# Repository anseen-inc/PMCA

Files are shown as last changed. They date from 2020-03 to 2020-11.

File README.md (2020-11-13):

# ポケットMCA（PSoC）
ポケットMCA（PSoC）（以下PMCA）は、PSoC 5LPを用いた簡易Multi Channel Analyzer (MCA)です。
MCA機能をPSoC内のブロックで構成し外付け部品を極力廃しているため、[CY8CKIT-059 PSoC® 5LP Prototyping Kit](https://www.cypress.com/documentation/development-kitsboards/cy8ckit-059-psoc-5lp-prototyping-kit-onboard-programmer-and)に1μFの容量と1kΩの抵抗を加えることでMCAとして動作します。

## 入力信号経路

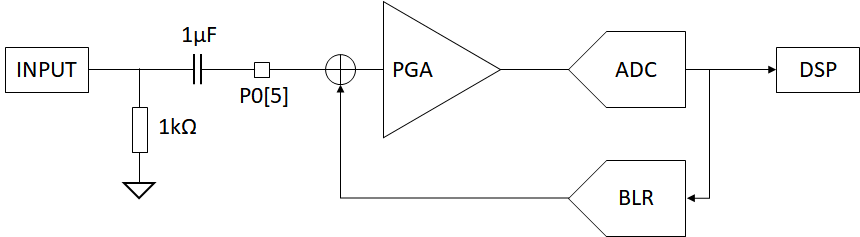
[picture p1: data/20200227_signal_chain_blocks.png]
信号経路

この図はPSoC内を含めた入力信号経路を示しています。
AC結合された入力信号はPGA（Programmable Gain Amplifier）で増幅した後、ADCでデジタル化されます。
デジタル化された信号は後段のDSP（Digital Signal Processing）ブロックに渡され、波高値情報が抽出されます。
並行してBLRブロックにもデジタル値が渡され、PGAの入力にフィードバックすることでベースライン電位が再設定されます。

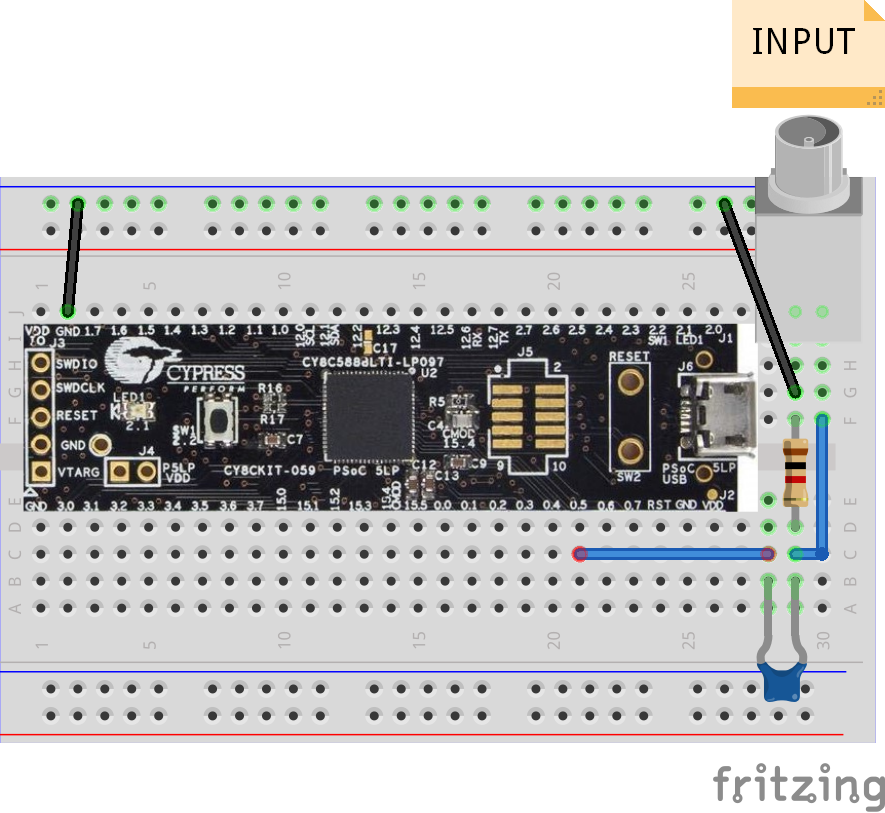
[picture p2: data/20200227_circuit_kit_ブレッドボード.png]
Prototyping Kitを用いる場合の接続

Prototyping KitでMCAを構成する場合には、図のように1μFの容量と1kΩの抵抗を入力端子に接続してください。

## 仕様

|項目|値|補足|
|:--|:--|:--|
|電源電圧|5V±0.25V|USBハイパワーポートの範囲（4.75V~5.25V）|
|消費電流（MCA)|20mA||
|入力電圧範囲|±10V|AC結合容量に依存|
|信号電圧範囲|±2Vpp max.|ゲイン2倍時|
|ピークタイム|10μs以上|満たない場合でも測定は可能|
|最大カウントレート|100kcps||

## 使い方
PMCA用の[ファームウェア書き込み](#HEXファイル書き込み)後、Windows PCとUSBケーブルで接続することでCOMポートとして認識されます。
そのCOMポートに対してASCIIコードを送ることでPMCAと対話でき、動作の変更や測定が行えます。
最初のアルファベットでコマンド種別を選択し、続く16進数（0~F）で設定値を指定します。
設定値がある場合は制御コマンド、ない場合は読み出しコマンドとして判断されます。
最初のアルファベット、コマンド指定以降の16進数以外は無視されます。

コマンドの例

```
SA # 10秒の測定を開始
S A # 上と同じ
V 3FC # HVを1020Vに設定
V # HV出力のモニタ結果を読み出す
```

PCから送信するコマンドの終端は改行（CR）です。
PMCAから送信するデータの終端は4 byte NULL（0x00000000）となっており、NULL終端文字列として取り込めます。
実際には端末エミュレータ互換のためNULLの前に改行（CR）が存在します。
加えて、データの成否を表す'OK/NG'の文字列が追加されるため、実質的な終端は7 byteになります。

### サンプルスクリプト
example.pyとexample_gui.pyがそれぞれCUI、GUIのサンプルスクリプトです。
必要な外部パッケージは以下のとおりです。

- pySerial
- numpy
- matplotlib

### 測定結果について
'S'コマンドで測定を開始すると1秒おきに測定結果が出力されます。
結果は2次元ヒストグラム（横軸：ADCチャネル、縦軸：頻度）のバイナリデータ（16 bit × 4096 ch）と終端7 byteです。
データ中の終端NULLを回避するため頻度値は測定値+1で表されます。

### 制御コマンド一覧

コマンド | 制御対象 | 設定範囲 | 初期値 | 詳細
------- | ------- | -------- | ----- | ----
A | | | | 予約
B | | | | 予約
C | | | | 予約
D | ベースライン電圧 | 0~4080 | auto | mVで指定。通常は自動で最適値に設定される。強制上書き用
E | 測定強制終了 | | | 測定を即時終了させる。使用しないが設定値が必要。
F | フィルタ | 0~3 | １ | ADC測定値に対する指数移動平均数の指定。指数移動平均係数α=2/(N+1)に対して、0:N=1, 1:N=3, 2:N=7, 3:N=15。
G | ゲイン | 2~16 | 2 | ゲインが設定値倍となる。
H | ハードウェア情報 | | | （予約）ハードウェア情報を送信するようリクエストを送る
I | ADC | 0 or 1 | 0 | 設定値が1の時、計測されたデジタル値の符号を反転する（負パルス用）
J | | | | 予約
K | | | | 予約
L | LLD/ULD | 0~4095 | 4095/4095 | 上位2bitで設定対象を指定（0b00:LLD, 0b01:ULD, 0b02:予約, 0b03:予約)。下位12bitで設定値を指定（パルス高ウィンドウ[ch]）。
M | 信号モニタ | | | （予約）信号モニタ機能
N | | | | 予約
O | HV | 0 or 1 | 0 | 0: OFF, 1: ON
P | | | | 予約
Q | | | | 予約
R | | | | 予約
S | 測定開始 | 0~2^16-1 | | 測定時間[秒]を指定して測定を開始する
T | | | | 予約
U | | | | 予約
V | HV出力電圧 | 0~1020 | 0 | Vで指定。
W | | | | 予約
X | 波高値計測アルゴリズム | 0～3 | 1 | 0:高速判定、1:立ち上がり高速＋上ピークホールド、2: 上下ピークホールド、3:BLR基準
Y | DSP | 0~2 | 0 | 計測モードの選択。0: ヒストグラム, 1:オシロスコープ（フリーラン）, 2:オシロスコープ（トリガー）
Z | | | | 予約

## 読み出しコマンド一覧

コマンド | 対象 | 戻り値 | 詳細
------------- | ------ | ------------ | ------
A | | | 予約
B | BLR | 0~4080 | BLRにより設定しようとしているベースラインのADCチャネル値を返します。
C | | | 予約
D | BLR | 正負の整数 | BLRにより加えたオフセットチャネル数を返します。
E | | | 予約
F | | | 予約
G | | | 予約
H | PMCA | 文字列 | PMCAの初期化処理を実行し、ハードウェア情報を文字列で返します。
I | | | 予約
J | | | 予約
K | | | 予約
L | | | 予約
M | | | 予約
N | | | 予約
O | | | 予約
P | | | 予約
Q | | | 予約
R | | | 予約
S | | | 予約
T | | | 予約
U | | | 予約
V | HVモニタ | 電圧値 | HV出力のモニタ結果を電圧で返します。
W | | | 予約
X | | | 予約
Y | | | 予約
Z | PMCA | なし | Bootloaderを起動します。PSoC CreaterのBootloader Host機能から新しいファームウェアを書き込むことが出来ます。

# ファームウェア書き込み
最初の1回のみPSoC Programmerを使いHEXファイルを書き込みます。
このときはPrototyping KitのKitProg側USB端子を使用する必要があります。
HEXファイル書き込み以降は'Z'コマンドでBootloaderに入ることでmicro USB端子からファームウェアを更新出来ます。

## HEXファイル書き込み
PSoC Programmerを用い、Prototyping KitのKitProg経由でHEXファイルを書き込みます。
HEXファイル書き込み後COMポートとして認識されMCAとして動作します。
HEXファイルにcyacdファイルが含まれているため[cyacdファイルの書き込み](#ファームウェア更新)は不要です。

1. KitProgを選択
1. 書き込むHEXファイルを指定
1. 書き込み実行

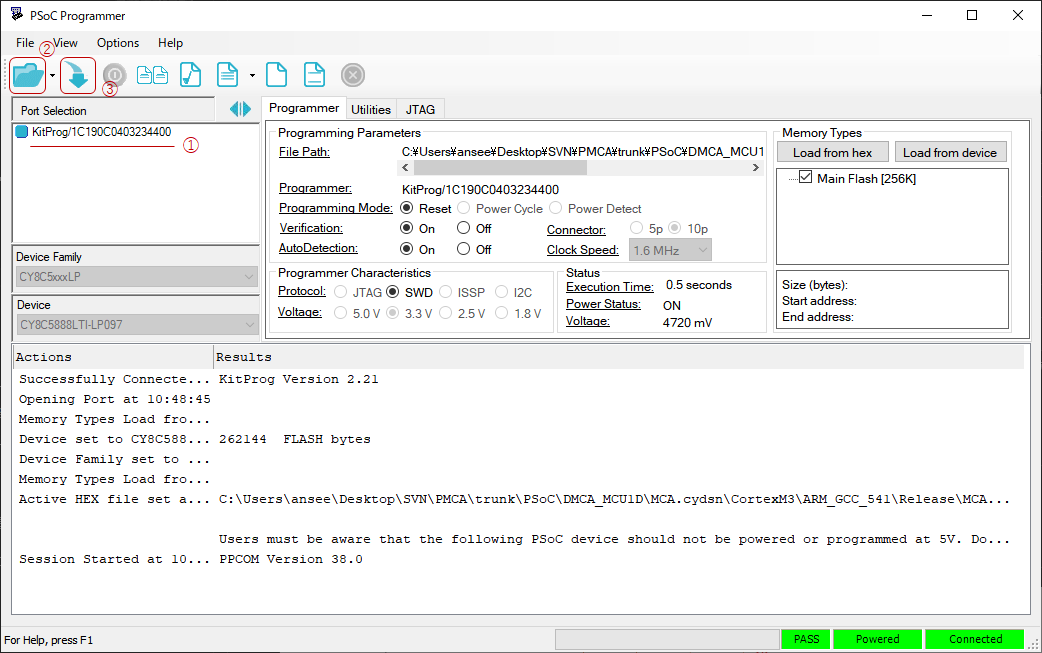
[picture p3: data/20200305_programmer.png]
PSoC Programmerによるファームウェア書き込み


## ファームウェア更新
通常使用時と同じくmicro USB端子経由でUSB接続します。
COMポートに接続し、'Z'コマンドを送信してbootloaderに入ります。
PSoC Createorのメニュー[Tools] -> [Bootloader Host...]からBootloader Hostを起動しcyacdファイルを書き込みます。

1. 'Z'コマンドでBootloaderに入る（pythonやTera Term等を使用）
1. Bootloader HostでUSB Human Interface Deviceを選択
1. 更新用のcyacdファイルを指定
1. 書き込み実行

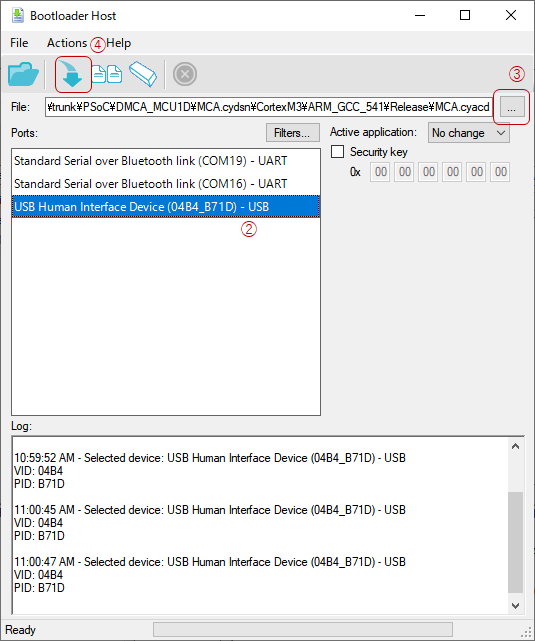
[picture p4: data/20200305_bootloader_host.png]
Bootloader Hostによるファームウェア更新


# 測定例

## <sup>241</sup>Am
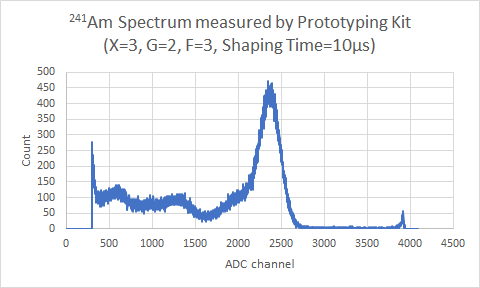
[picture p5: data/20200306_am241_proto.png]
<sup>241</sup>Amのスペクトル測定結果


# ANS-PMCAについて
ポケットMCA用にPSoC 5LP基板をおこしたものがANS-PMCAになります。
ANS-PMCAにはMCA機能に加え、

- 高電圧出力（+/-1000V）
- 電源およびUSB通信の絶縁

が備わります。

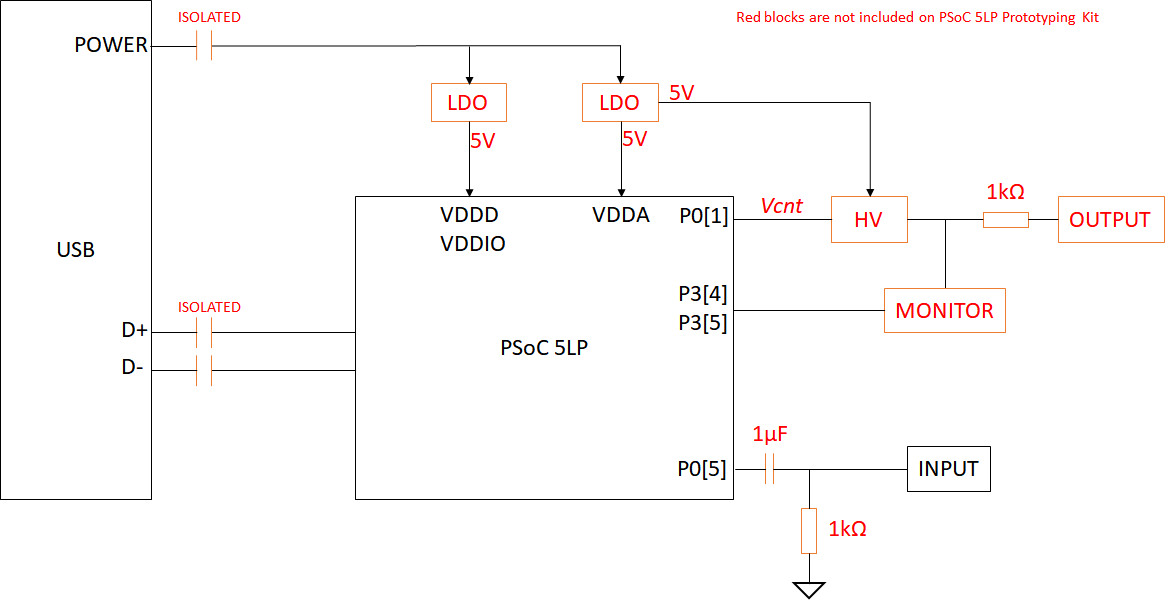
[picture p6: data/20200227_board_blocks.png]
PSoC 5LPとその周辺回路

この図はANS-PMCAのブロック図を示しています。
赤で示した箇所がANS-PMCA版で追加される機能です。
電源はUSBバスパワーから供給されますが、絶縁した後にデジタル/アナログそれぞれLDOで分離されます。
高電圧生成器（HV）の制御はPSoCから行われ、SHVコネクタから出力されるとともにPSoCのDelta Sigma ADCにより電圧がモニタされます。
入力は1μFの容量でDC成分が除去され、PSoC内部ではBLR（Base Line Restorer）機能により適切なベースライン電位が再設定されます。

Prototyping Kitを用いたPMCAとの機能的な違いはHVブロックの有無です。
回路的にはUSBの絶縁、高電圧生成回路、高電圧モニタ回路、入力容量、負荷抵抗、電源回路の有無が異なり、雑音特性が改善されています。
例えば、無信号時の波形において電圧雑音がPrototyping Kitを用いたPMCAでは3.0 [ch rms]なのに対して、ANS-PMCAでは0.6 [ch rms]と1/5に改善されています。

## Prototyping Kitを用いたPMCAの無信号波形
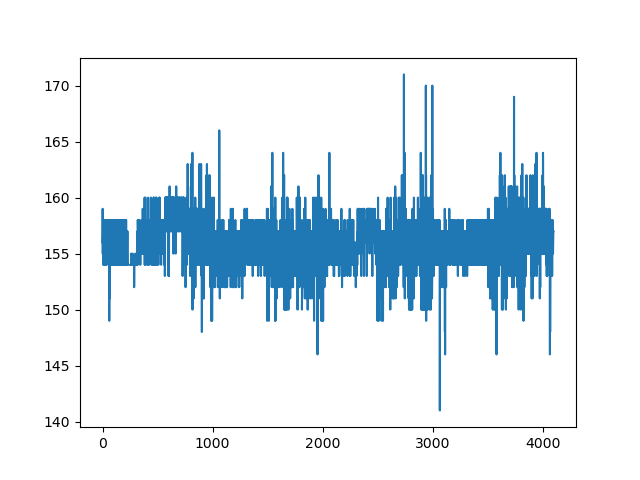
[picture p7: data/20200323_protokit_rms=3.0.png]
Prototyping Kitの無信号波形


## ANS-PMCAの無信号波形
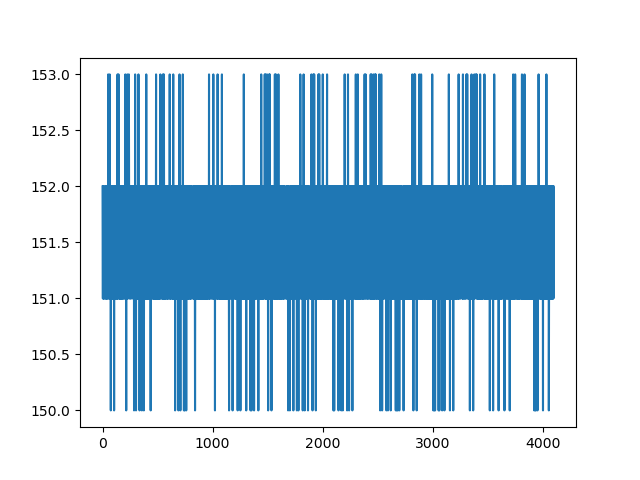
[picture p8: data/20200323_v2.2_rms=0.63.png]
ANS-PMCAの無信号波形


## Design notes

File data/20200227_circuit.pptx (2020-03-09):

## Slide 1

USB

POWER

ISOLATED

Red blocks are not included on PSoC 5LP Prototyping Kit

LDO

LDO

5V

5V

VDDD
VDDIO

5V

PSoC 5LP

VDDA

P0[1]

P3[4]
P3[5]

Vcnt

HV

1kΩ

OUTPUT

D+

ISOLATED

MONITOR

D-

P0[5]

1μF

INPUT

1kΩ

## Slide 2

INPUT

1μF

PGA

ADC

BLR

DSP

1kΩ

P0[5]

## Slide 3

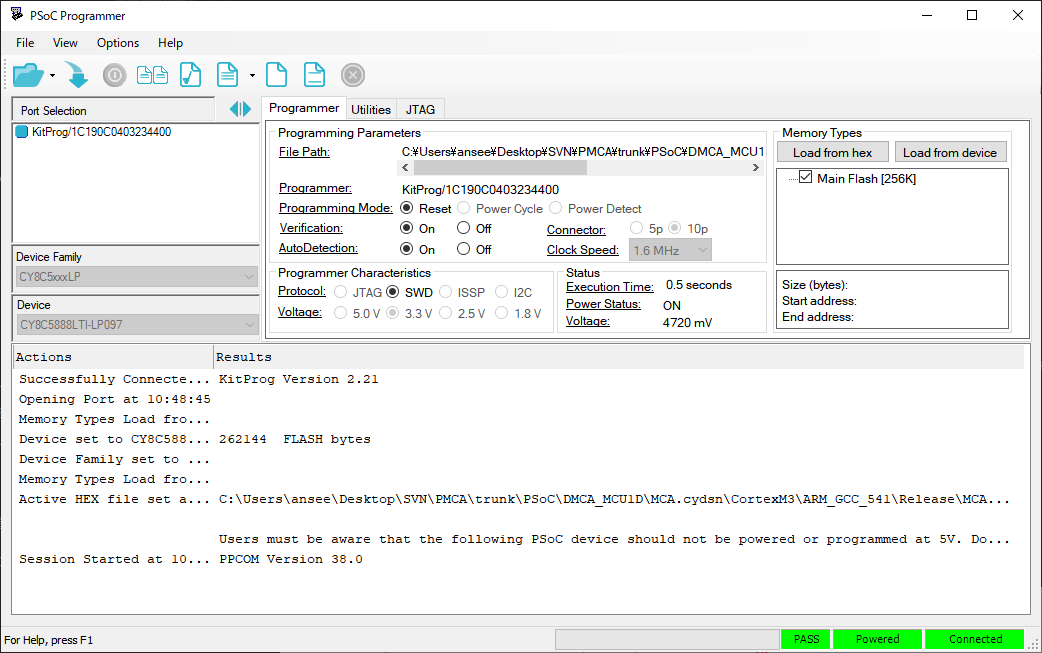
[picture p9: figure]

②

③

①

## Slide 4

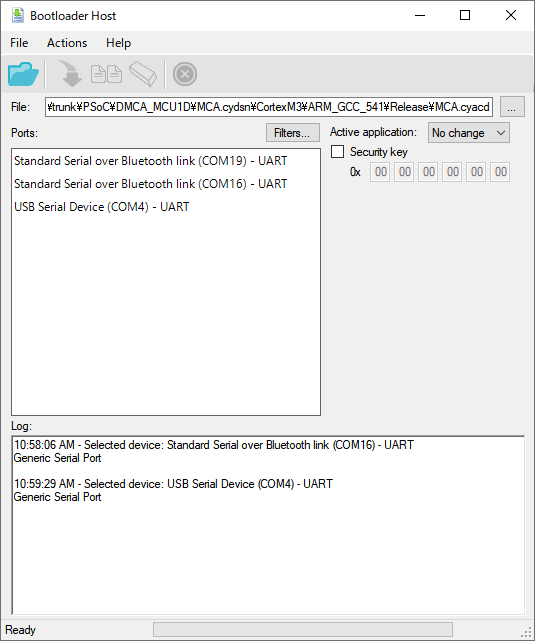
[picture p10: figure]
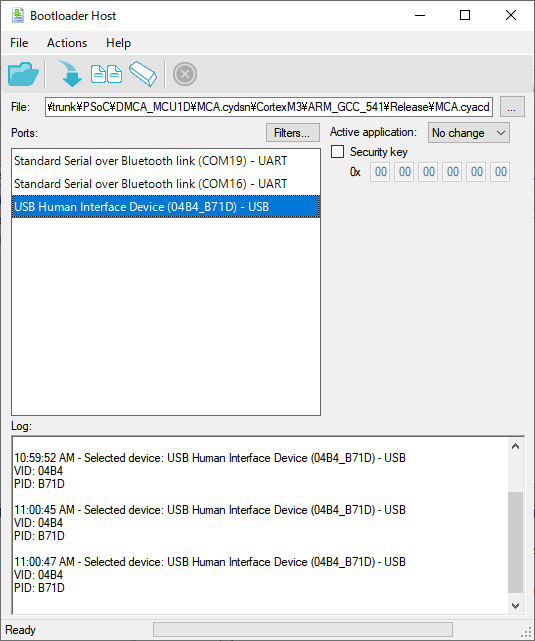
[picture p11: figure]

④

③

①

②

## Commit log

2020-03-09 ファームウェア初版
2020-03-17 終端コード修正。バイナリ制御削除
2020-03-24 GUIサンプル作成
2020-03-24 基板2.2の情報で更新
    [20200323_Am241_F0_v2.2.csv, 20200323_Am241_F3_v2.2.csv]
2020-11-13 初期値を追加
2020-11-13 初期設定を修正
2020-11-13 Firmware version: Nov 13 2020 17:01:58 測定と通信の同期を改善
2020-11-18 グラフ更新時のautoscaleを修正
2020-11-18 初期値修正
2021-02-22 ゲイン変更テストスクリプトを追加
2021-11-30 計測用メモリを増やしてデータ欠損を防止
2024-10-08 Support board v2.4
